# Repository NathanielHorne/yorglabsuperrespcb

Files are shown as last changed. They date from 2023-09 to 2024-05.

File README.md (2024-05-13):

# yorglabsuperrespcb

# Table of Contents
1. [SUMMARY](#SUMMARY)
2. [PCB](#PCB)
3. [CODE](#CODE)
4. [OPERATION](#OPERATION)

## SUMMARY
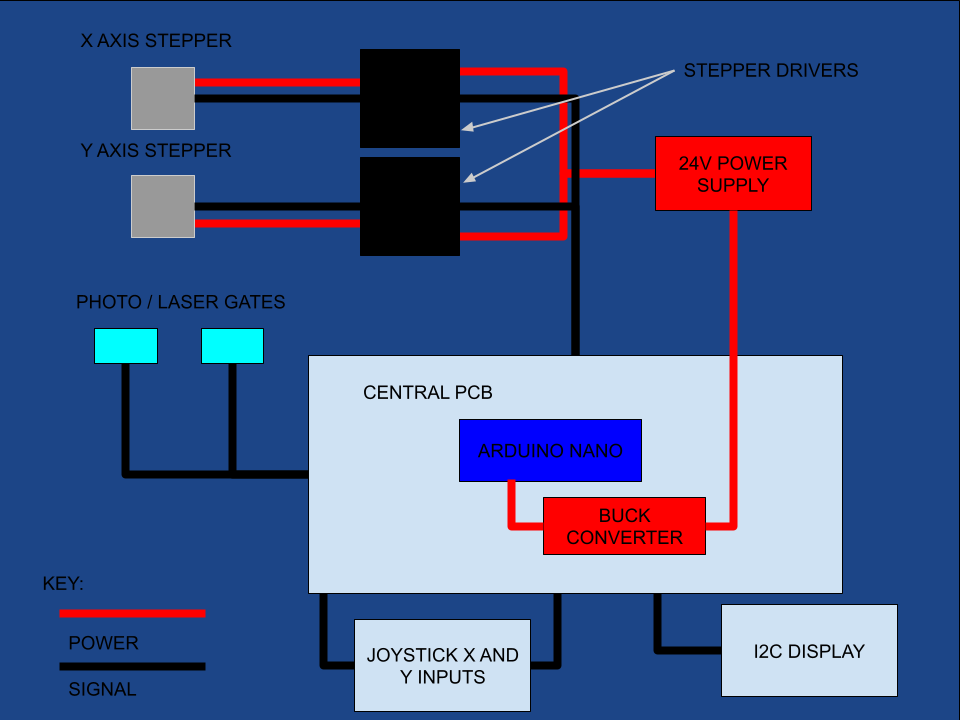
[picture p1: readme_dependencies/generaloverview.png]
Project overview

## PCB
  ### Overview
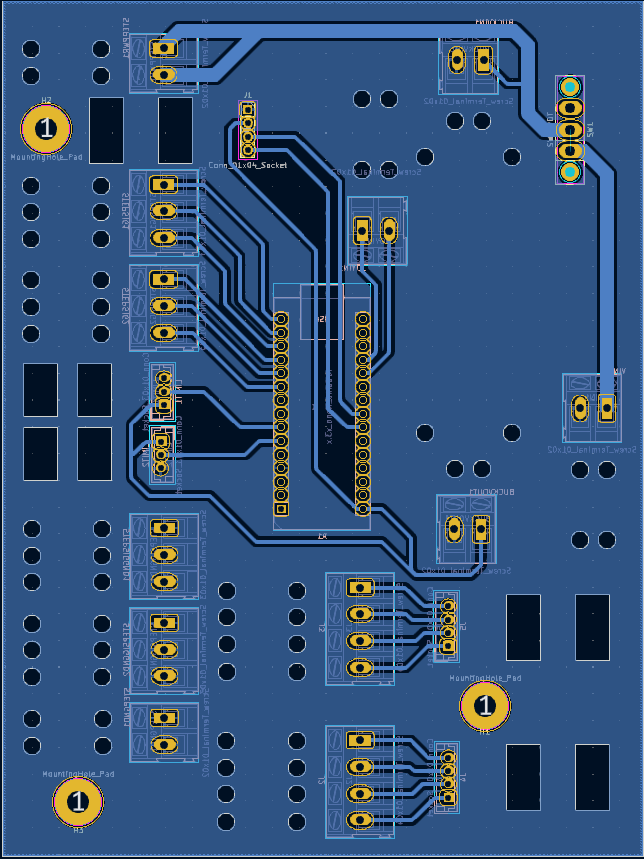
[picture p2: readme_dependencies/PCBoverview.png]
PCB overview
  
  
  The PCB looks nasty, but is more simple than it appears, at first.
  ***
  ### Where Was it Milled?
  Just as some general background, the board was milled and cut out at the BYU Electrical Engineering Experiential Learning Center. At the time of manufacture, they had yet to integrate solder masks. So, any pictures given of the fully-assembled board will show only *bare copper*. Future iterations should have a solder mask for safety reasons.
  ***
  ### Tension Relief Holes
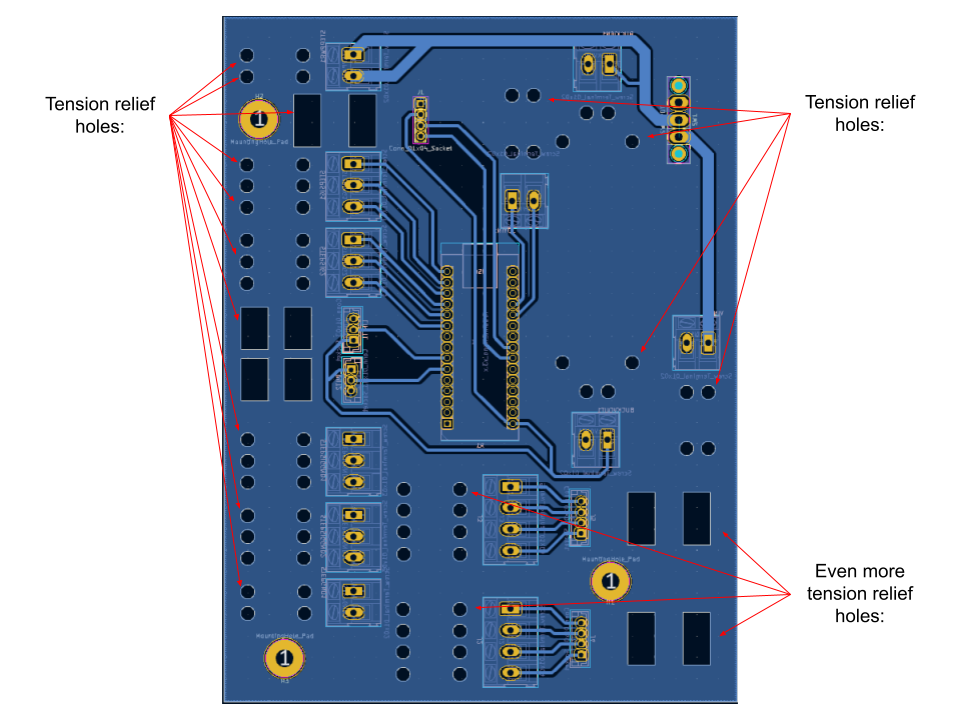
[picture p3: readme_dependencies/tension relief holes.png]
Tension relief holes indication
  
  
  Probably the most striking thing to see, at first, are the tension relief holes. You thread the wires or ribbon cables through them like a needle and thread. This makes it so that the tension of any motion / movement on the wires from the outside is transfered to the board instead of the connectors. This adds durability to the board, but also makes it so that it's more complicated to manufacture. Luckily, the BYU Electrical Engineering Experiential Learning Center was able to mill it with little issue.
  ***
  ### Mounting Holes
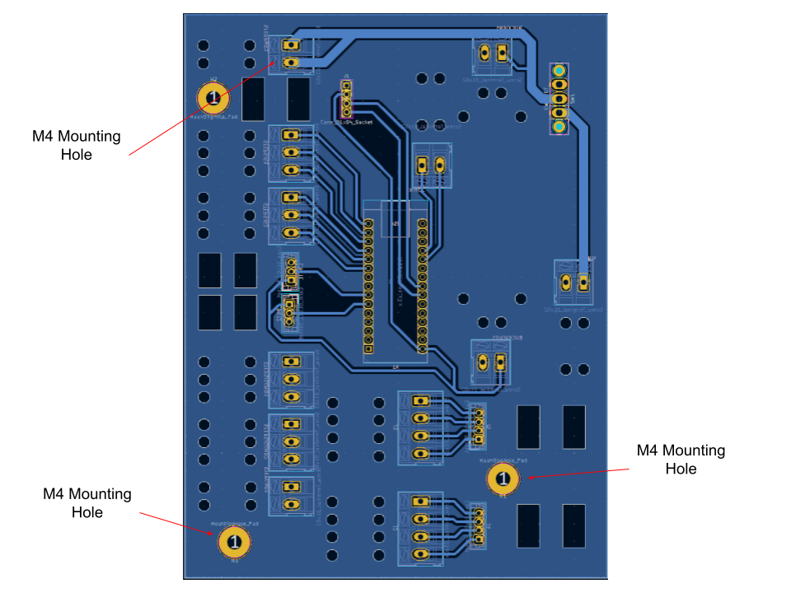
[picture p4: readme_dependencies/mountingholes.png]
Mounting holes identification
  

  These help mount the PCB to a backing plate. These aren't utilized in our current setup.
  ***
  ### Power Network
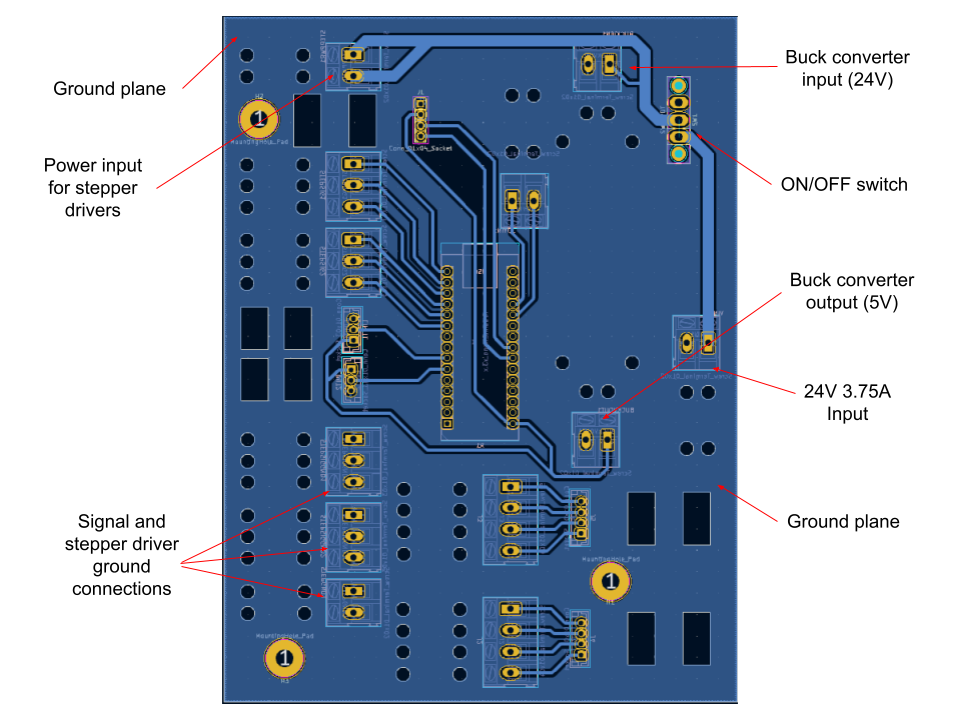
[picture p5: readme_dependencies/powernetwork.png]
Power network identification
  
  ***
  ### Signal Network
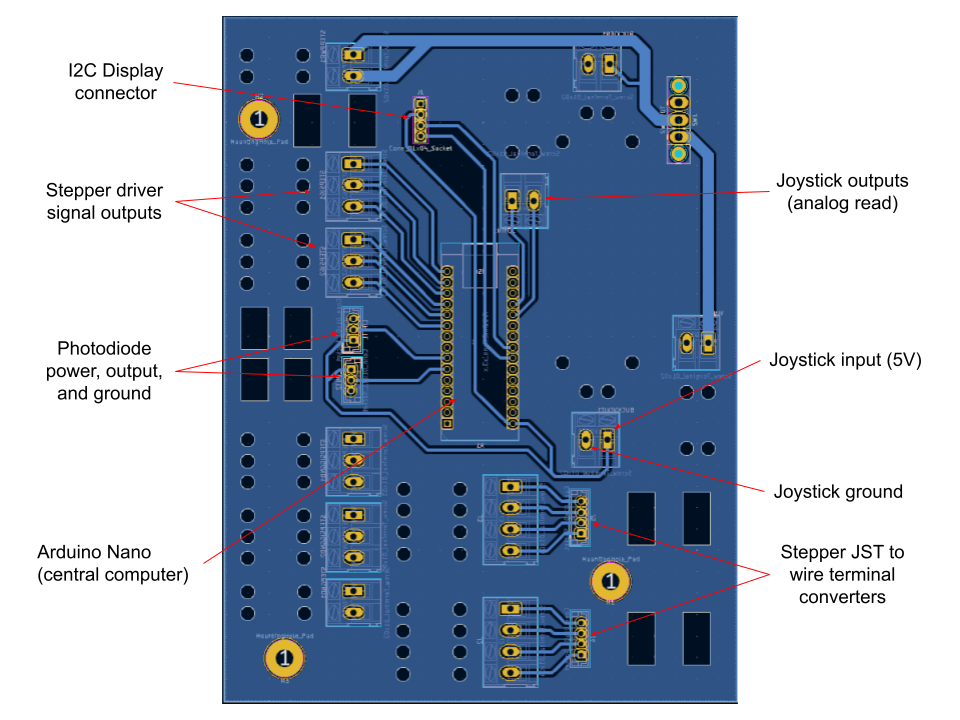
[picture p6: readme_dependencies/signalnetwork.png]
Signal network identification
  
  
  A note about the joystick: the joystick is comprised of two potentiometers (variable resistors). The Nano is able to convert voltage inputs from 0V - 5V and convert it to a value of 0 - 1024 using `analogRead([pin name])`. By running the output of the variable end of the potentiometer to a pin corresponding to the X and Y axis, we're able to measure the angle at which the joystick is currently at. This helps to inform the speed each motor takes on. The more extreme the angle of the joystick on a particular axis, the faster the motor on that particular axis is.
  ***

## CODE
  ### Limitations
  The code isn't perfect. Memory leaks and other performance issues may exist. In addition, the code doesn't neccessarily *need* to be in a single file. Other issues may exist to others. Input in the "issues" page of this repo would be much appreciated. Because an arduino nano cannot support multithreading, minimizing memory leaks and improving speeds are paramount.

  The photogates also aren't used, currently. Therefore, there is no safety preventing the device from moving beyond its intended limits. This is a *major* bug that needs to be fixed immediately.
  ***
  ### Methodology
  In general, any variable used is either inumerated using the `#define` command or is passed by reference. This helps improve the speed at which the code iterates and the amount of memory used. These things can still be improved upon, however.
  ***
  This code is broken up into three distinct sections: perception, planning, and action.
  ```cpp
  perception();
  ```
  This is where the inputs from the various sensors the nano uses are measured and saved. Currently, just the input of the joystick is read, but in the future, this is where one would check whether or not the laser gates are tripped or not, for example.
  ```cpp
  planning();
  ```
  This is where actions are prepped. In our case, this is where the direction and speed of the stepper motors is calculated.
  ```cpp
  action();
  ```
  In this section, the nano executes the actions we had prepared.
  
  *Every other method in the code is an appendage to these three methods*
  
  ***
  ### Startup
  An attempt was made to create a movement sequence that would automatically "home" the stage, setting the stepper's default state to one extreme of their movement. This would allow the laser gates to prevent the stage from moving beyond their limits. This was never acheived. This also makes it so that the I2C display doesn't display location information (another desired goal with startup)
  ### Custom Step Signal
  In order for each stepper to increment, the "step" pin needs to receive a distinct off-on-off pattern. The rate at which these patterns come in dictates the rate at which the stepper increments, changing its speed. 
  The Arduino Nano's hardware natively supports "pulse width modulation" (PWM) that *could* be used to accomplish this. However, PWM signals are generally set at a specific frequency. This would make it so that the steppers would step at a fixed rate regardless of the joystick's orientation. 
  
  Because of these limitations, a way of delivering this signal was created using the Nano's internal clock and digital pins:
  ```cpp
  void move_stepper(const unsigned int& step_pin, unsigned long& time_index, const unsigned int& time_tolerance, const unsigned int& direction_bool, int64_t& num_steps, const int& ena) {
    if ((micros() - time_index) > time_tolerance) {
      digitalWrite(step_pin, HIGH);
      digitalWrite(step_pin, LOW);
      if (ena == LOW) {
        if(direction_bool == HIGH) {
          num_steps++;
        }
        else if (direction_bool == LOW) {
          num_steps--;
        }
      }
      time_index = micros();
    }
  }
  ```
  At its core, this method manually defines how long the arduino takes in-between stepping each motor. This is done by storing when the nano begins to wait using the `micros();` command, then measuring how much time has past. If the elapsed time is larger than the defined wait time, the nano commands the stepper to take a single step, the number of total steps that stepper has taken is recorded, and the process begins again. 
  The wait time is defined at the very top of the file. See the variables `slowest_speed`, `second_fastest`, `second_slowest`, and `fastest_speed` in the `#define` section of the code.
  ***
  ### A Note About Printing the Relative Position of the Stage
  In the event that we wanted to plot the relative position of the stage, we would need to display the number of steps the stepper has taken in relation to when it was homed. Turns out, the number of steps a stepper takes traversing accross one of the metal fins the photodiode uses to tell whether or not the stepper is out of alignment is about the max value of the variable type "long long" or "int64_t". Obviously, this is kind of insane. It also leads to other errors. 
  ***
## OPERATION
Ensure every wire is connected to where it needs to be connected to. Position the stage so the path of the photodiodes is blocked by their corresponding metal fin. Plug the stage's power supply into a wall socket. Turn the motherboard on by flipping the switch. A blue and red indicator light from the buck converter and Arduino Nano respectively should come on immediately. From then on, use the joystick to move the stage. The higher the angle of the joystick in either direction, the faster the steppers will step in that direction.

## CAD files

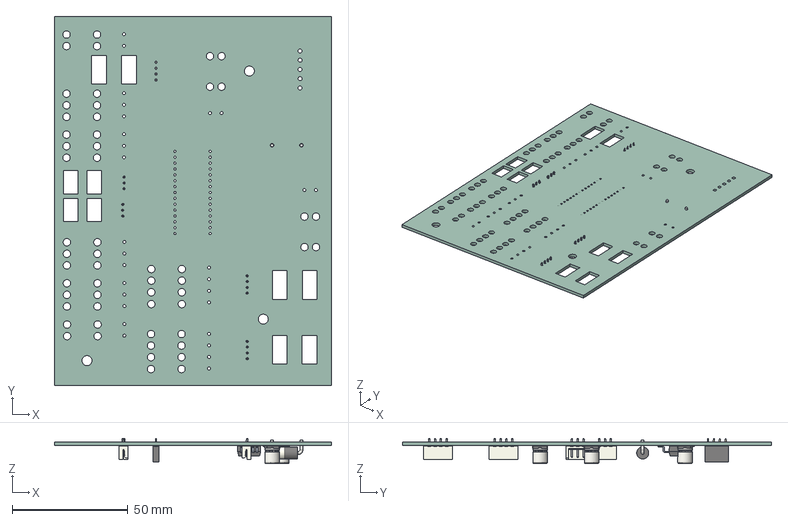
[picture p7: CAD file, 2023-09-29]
stepper_stage_PCB/stepper_microscope_stage/stepper_microscope_stage.step
119.9 x 159.6 x 10.9 mm
stepper_microscope_stage PCB

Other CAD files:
stepper_stage_PCB/assembly_outputs/3Dprintedsolderstencil/stepper_microscope_stage-B_Paste.dxf

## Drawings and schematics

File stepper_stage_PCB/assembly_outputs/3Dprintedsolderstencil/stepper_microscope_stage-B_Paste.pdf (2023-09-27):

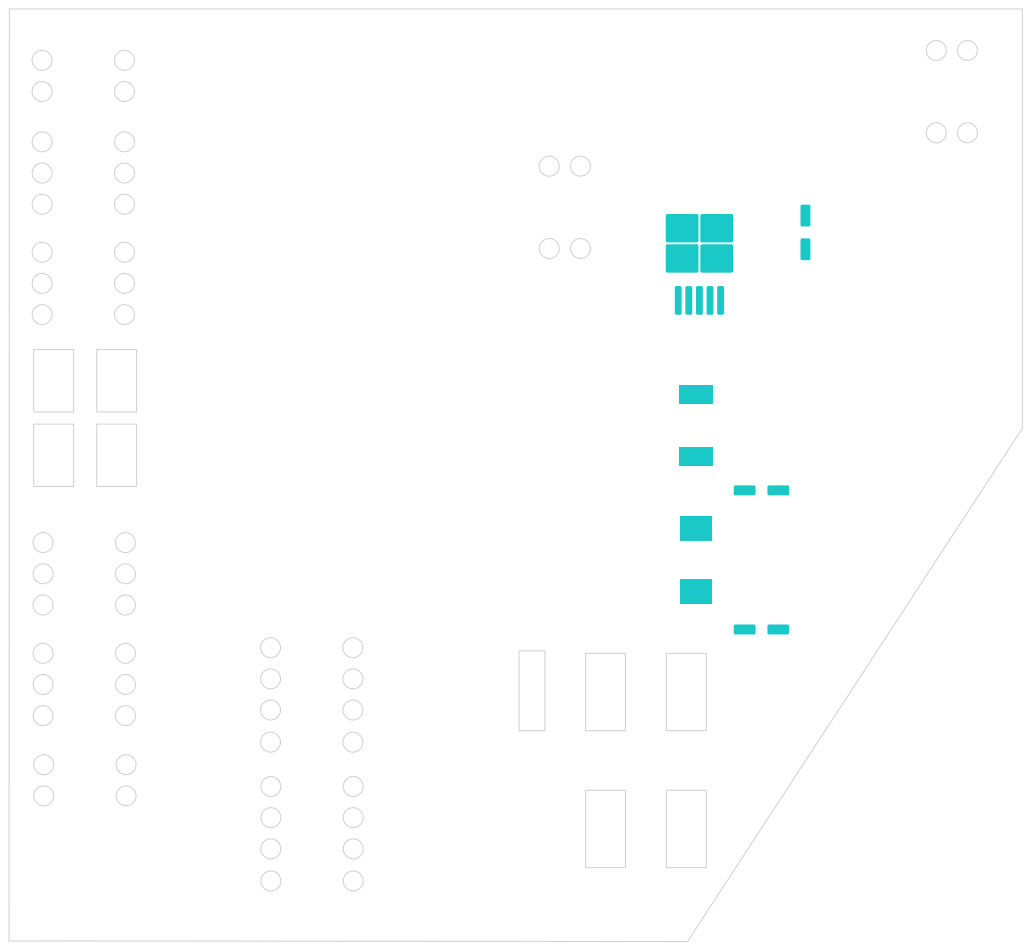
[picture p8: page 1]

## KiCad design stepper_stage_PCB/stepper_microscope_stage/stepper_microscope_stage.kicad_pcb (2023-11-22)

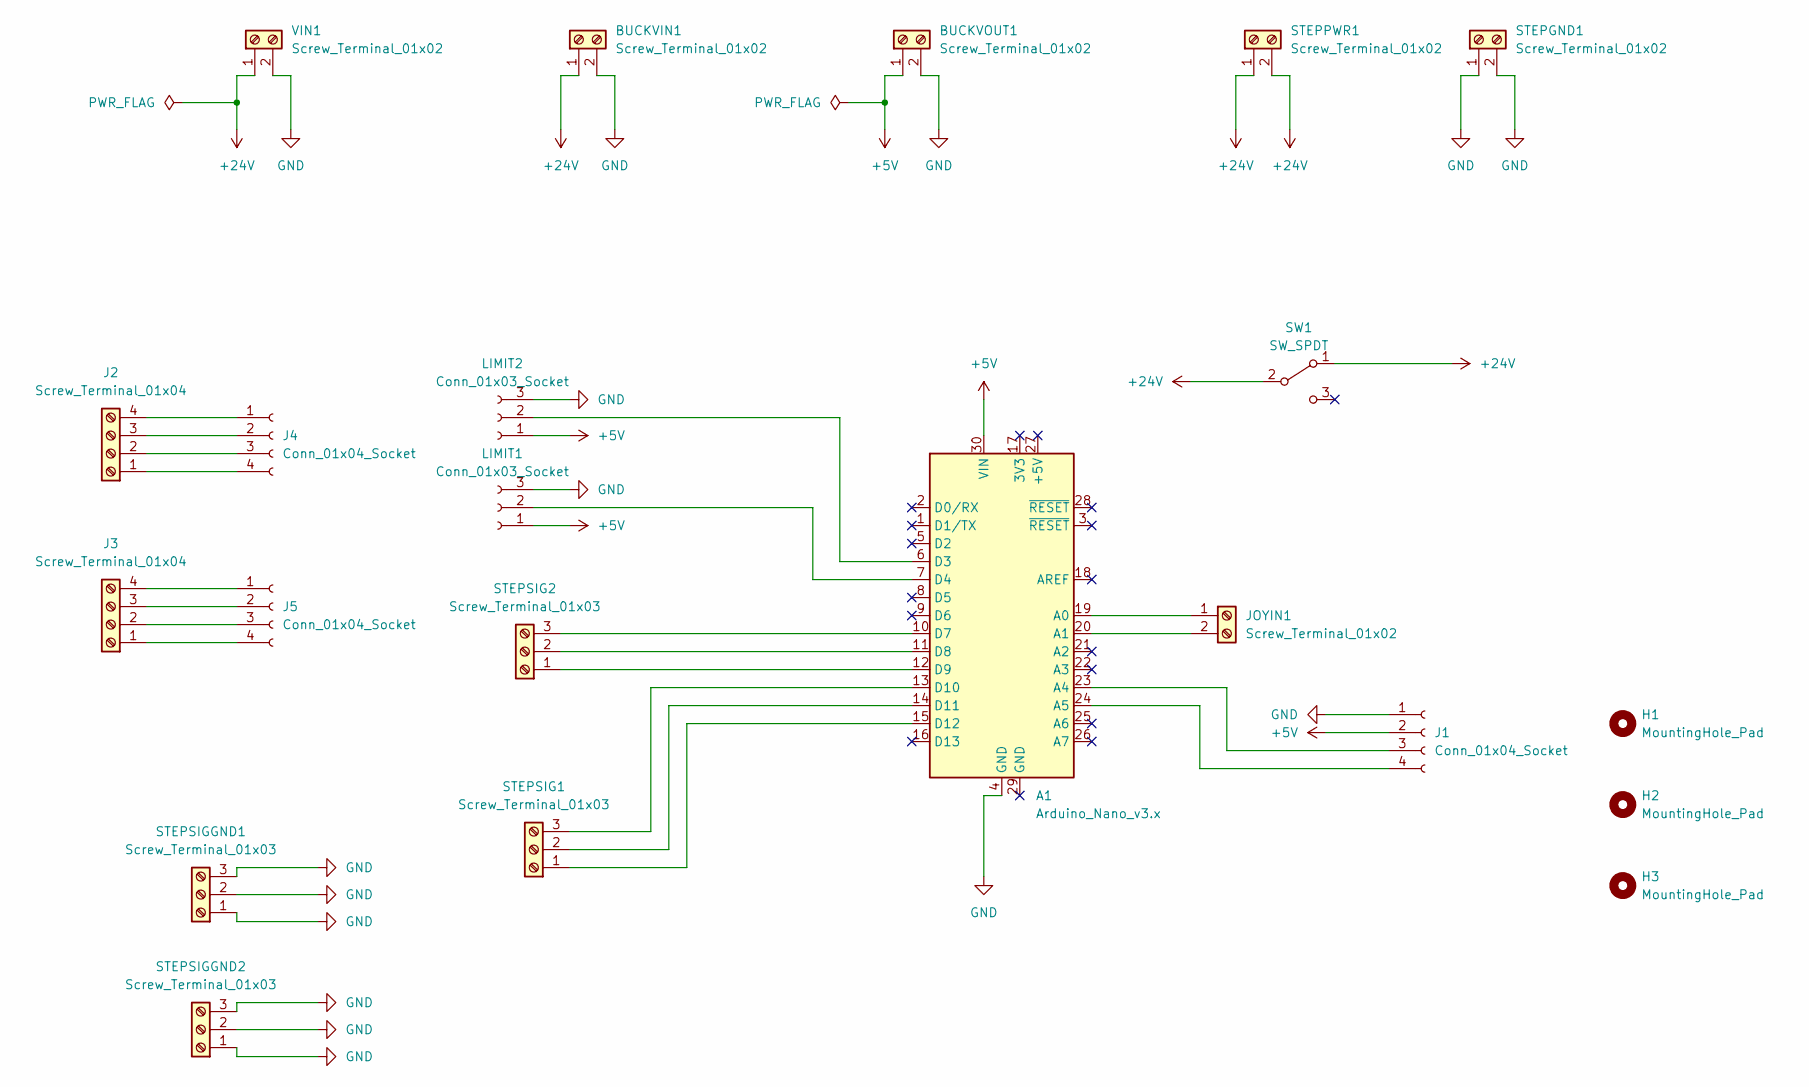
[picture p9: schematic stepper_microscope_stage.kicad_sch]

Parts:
A1: Arduino_Nano_v3.x; Arduino_Nano
BUCKVIN1: Screw_Terminal_01x02; TerminalBlock_Altech_AK300-2_P5.00mm
BUCKVOUT1: Screw_Terminal_01x02; TerminalBlock_Altech_AK300-2_P5.00mm
H1, H2, H3: MountingHole_Pad; MountingHole_4.3mm_M4_Pad
J1: Conn_01x04_Socket; PinSocket_1x04_P2.54mm_Vertical
J2, J3: Screw_Terminal_01x04; TerminalBlock_Altech_AK300-4_P5.00mm
J4, J5: Conn_01x04_Socket; JST_EH_B4B-EH-A_1x04_P2.50mm_Vertical
JOYIN1: Screw_Terminal_01x02; TerminalBlock_Altech_AK300-2_P5.00mm
LIMIT1, LIMIT2: Conn_01x03_Socket; JST_EH_B3B-EH-A_1x03_P2.50mm_Vertical
STEPGND1: Screw_Terminal_01x02; TerminalBlock_Altech_AK300-2_P5.00mm
STEPPWR1: Screw_Terminal_01x02; TerminalBlock_Altech_AK300-2_P5.00mm
STEPSIG1, STEPSIG2: Screw_Terminal_01x03; TerminalBlock_Altech_AK300-3_P5.00mm
STEPSIGGND1, STEPSIGGND2: Screw_Terminal_01x03; TerminalBlock_Altech_AK300-3_P5.00mm
SW1: SW_SPDT; spdt_4mm_pitch_with_tension_relief
VIN1: Screw_Terminal_01x02; TerminalBlock_Altech_AK300-2_P5.00mm

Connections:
+5V: A1.30 (VIN), BUCKVOUT1.1, J1.2, LIMIT1.1, LIMIT2.1
+24V: BUCKVIN1.1, STEPPWR1.1, STEPPWR1.2, SW1.1 (A), SW1.2 (B), VIN1.1
GND: A1.4 (GND), BUCKVIN1.2, BUCKVOUT1.2, J1.1, LIMIT1.3, LIMIT2.3, STEPGND1.1, STEPGND1.2, STEPSIGGND1.1, STEPSIGGND1.2, STEPSIGGND1.3, STEPSIGGND2.1, STEPSIGGND2.2, STEPSIGGND2.3, VIN1.2
unnamed: A1.19 (A0), JOYIN1.1
unnamed: A1.20 (A1), JOYIN1.2
unnamed: A1.23 (A4), J1.3
unnamed: A1.24 (A5), J1.4
unnamed: A1.6 (D3), LIMIT2.2
unnamed: A1.7 (D4), LIMIT1.2
unnamed: A1.10 (D7), STEPSIG2.3
unnamed: A1.11 (D8), STEPSIG2.2
unnamed: A1.12 (D9), STEPSIG2.1
unnamed: A1.13 (D10), STEPSIG1.3
unnamed: A1.14 (D11), STEPSIG1.2
unnamed: A1.15 (D12), STEPSIG1.1
unnamed: J2.1, J4.4
unnamed: J2.2, J4.3
unnamed: J2.3, J4.2
unnamed: J2.4, J4.1
unnamed: J3.1, J5.4
unnamed: J3.2, J5.3
unnamed: J3.3, J5.2
unnamed: J3.4, J5.1

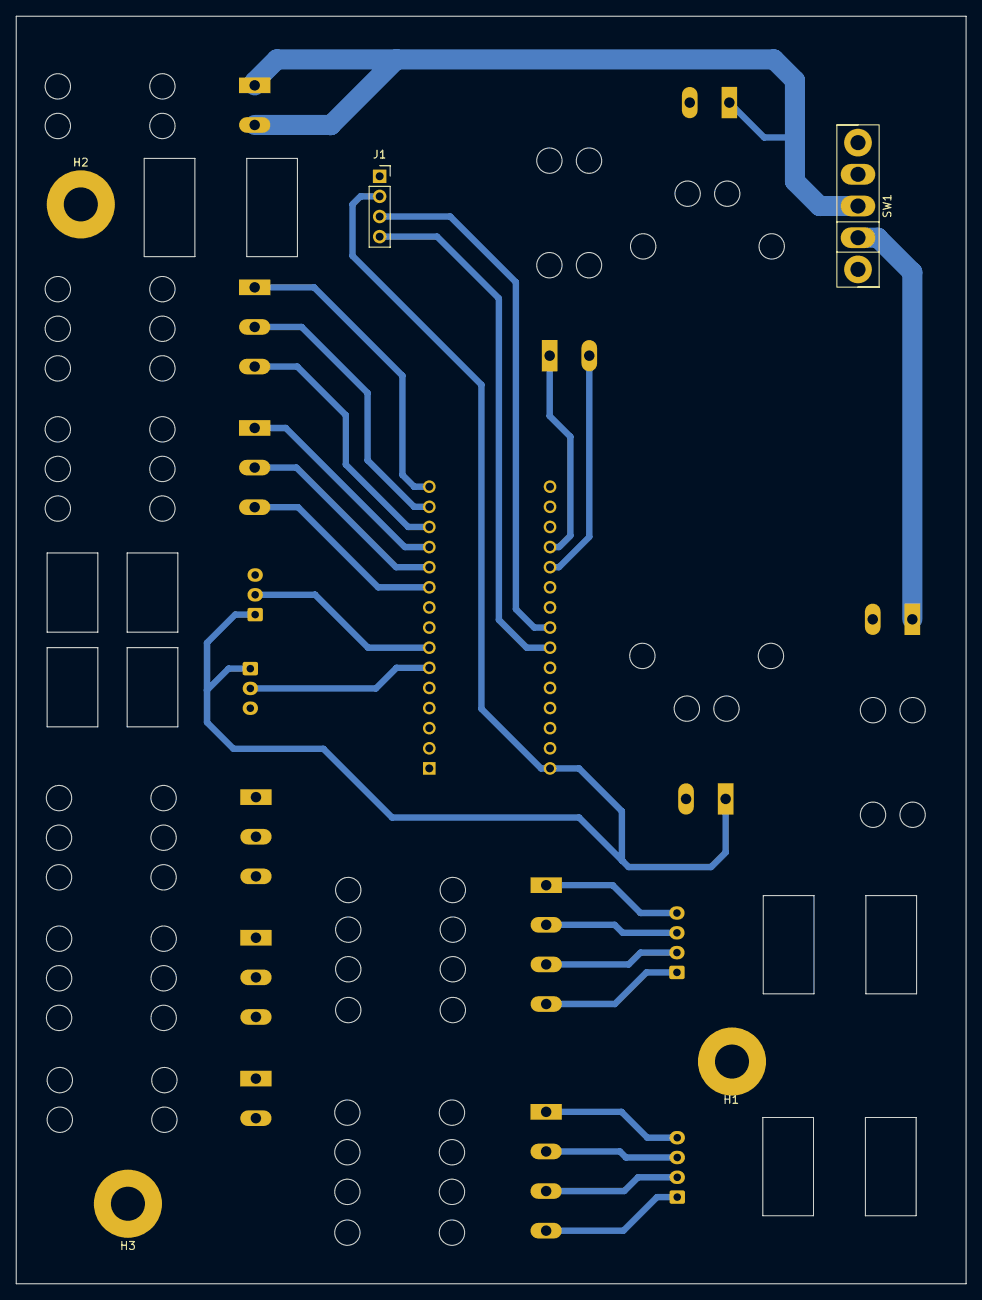
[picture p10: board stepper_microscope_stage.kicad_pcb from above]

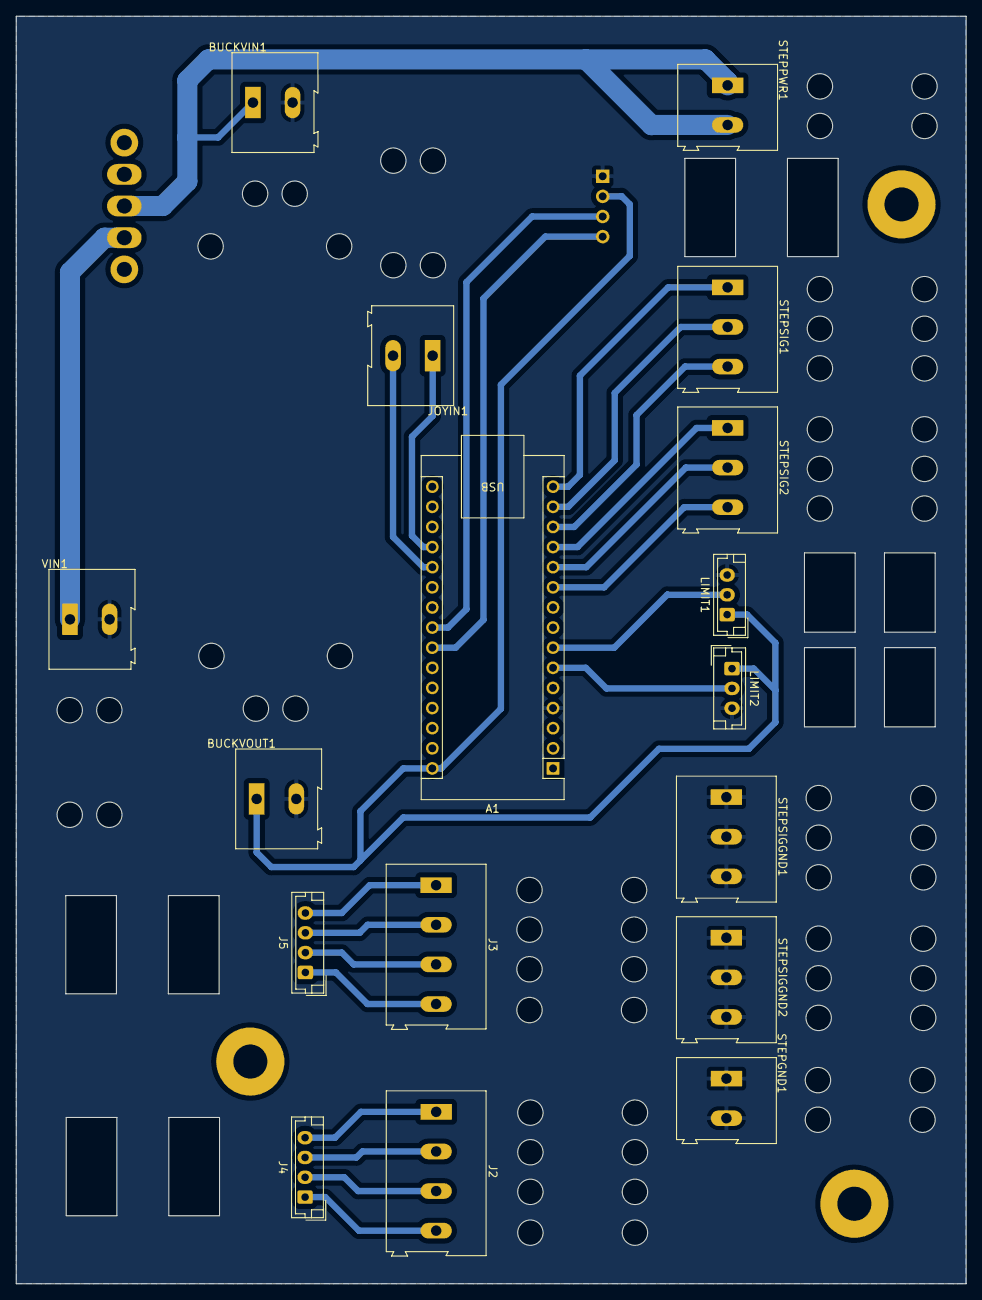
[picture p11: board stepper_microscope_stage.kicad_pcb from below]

Board: 2 copper layers, 119.9 x 160.0 mm, 22 parts (17 on the bottom side), 23 nets.

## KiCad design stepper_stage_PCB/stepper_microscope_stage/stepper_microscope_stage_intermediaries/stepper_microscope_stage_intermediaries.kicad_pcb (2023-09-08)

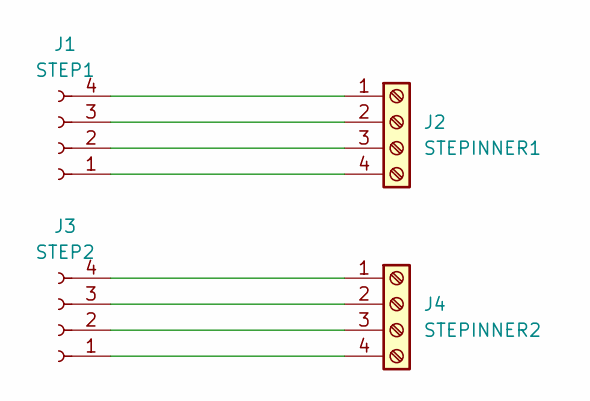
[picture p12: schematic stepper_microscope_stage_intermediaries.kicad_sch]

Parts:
J1: STEP1; Molex_CLIK-Mate_502382-0470_1x04-1MP_P1.25mm_Vertical
J2: STEPINNER1; TerminalBlock_Altech_AK300-4_P5.00mm
J3: STEP2; Molex_CLIK-Mate_502382-0470_1x04-1MP_P1.25mm_Vertical
J4: STEPINNER2; TerminalBlock_Altech_AK300-4_P5.00mm

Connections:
unnamed: J1.1, J2.4
unnamed: J1.2, J2.3
unnamed: J1.3, J2.2
unnamed: J1.4, J2.1
unnamed: J3.1, J4.4
unnamed: J3.2, J4.3
unnamed: J3.3, J4.2
unnamed: J3.4, J4.1

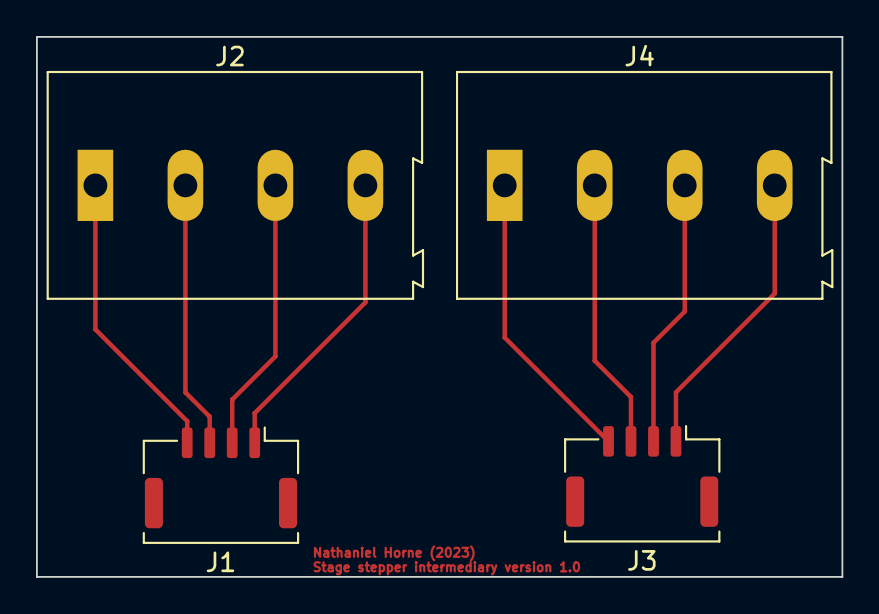
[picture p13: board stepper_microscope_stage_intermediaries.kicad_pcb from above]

Board: 2 copper layers, 44.8 x 30.0 mm, 4 parts (0 on the bottom side), 8 nets.

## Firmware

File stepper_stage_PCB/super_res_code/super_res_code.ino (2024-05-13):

#include <math.h>

// Stepper box 1 I/O pin definitions
#define stepPin1  10
#define dirPin1   11
#define enPin1    12

// Stepper box 2 I/O pin definitions
#define stepPin2  9
#define dirPin2   8
#define enPin2    7

// Dual axis joystick I/O definitions 
#define joy_in1   A1
#define joy_in2   A0

// Optical gate switches I/O definitions
#define gate_switch1 4
#define gate_switch2 3

// Proven deadzone = 200
#define joy_deadzone 200

#define analog_in_max_range   880
#define analog_in_half_range  analog_in_max_range/2

// How long the stepper should wait in microseconds between steps 
#define startup_speed         700
#define slowest_speed         7000
#define second_fastest        3500
#define second_slowest        1453
#define fastest_speed         700

// Any analog read value outside of this zone is automatically disregarded
#define movement_zone         (analog_in_half_range-joy_deadzone)

/* This defines different speed regions based on the joystick's angle
   This is based off of the joystick's angle from in the "middle" position
   The middle position is also 512 according to analogRead();
*/
#define limit_1               280
#define limit_2               360
#define limit_3               400

// Define the global variables for stepper 1 
unsigned int joy_input1 = 0;
int ena1 = LOW;
int direction_bool1 = LOW;
unsigned long step_1_time_index = micros();
unsigned int step_1_time_tolerance = 0;
int64_t num_steps1 = 0;
// These variables were supposed to be used during the initial startup sequence
// This seequence hasn't been perfected yet. 
int is_off_track1 = LOW;
int is_at_middle1 = LOW;

int midpoint = 0; 

// Define the global variables for stepper 2
unsigned int joy_input2 = 0;
int ena2 = LOW;
int direction_bool2 = HIGH;
unsigned long step_2_time_index = micros();
unsigned int step_2_time_tolerance = 0;
int64_t num_steps2 = 0;
int is_off_track2 = LOW;
int is_at_middle2 = LOW;

void get_joystick_inputs();

void get_is_off_tracks();

void get_back_on_track();

void set_direction_bools();

void set_en_pins();

void startup();

void perception();

void joystick_direction(const int& in, int& dir, int& ena, const int& off_track);

unsigned int stepper_wait_time(const int& input);

void planning();

void move_stepper(const unsigned int& step_pin, unsigned long& time_index, const unsigned int& time_tolerance, const unsigned int& direction_bool, int64_t& num_steps, const int& ena);

void action();

void print(uint64_t value);

unsigned int uint64_to_int(uint64_t value) {
  int return_value = 0;
  for (int i = 0; i < 2000; i++) {
    value /= 10;
  }
  return_value = value;
  return return_value;
}

void setup() {
  Serial.begin(9600);
  
  // Setup pins for stepper driver 1
  pinMode(stepPin1, OUTPUT);
  pinMode(dirPin1, OUTPUT);
  pinMode(enPin1, OUTPUT);
  
  // Setup pins for stepper driver 1
  pinMode(stepPin2, OUTPUT);
  pinMode(dirPin2, OUTPUT);
  pinMode(enPin2, OUTPUT);

  // Setup joystick inputs
  pinMode(joy_in1, INPUT);
  pinMode(joy_in2, INPUT);

  // Setup photodiode inputs
  pinMode(gate_switch1, INPUT);
  pinMode(gate_switch2, INPUT);
  
  // Enable stepper driver
  set_en_pins();

  // Set stepper driver directions
  set_direction_bools();

//  startup();
}

void loop() {
  // This is the core of the code. The Nano repeats this code indefinitely

  perception();

  planning();

  action();
}

void get_joystick_inputs() {
  joy_input1 = analogRead(joy_in1);
  joy_input2 = analogRead(joy_in2);
}

void get_is_off_tracks() {
  // Determines whether or not the photodiodes on each axis are triggered or not

  is_off_track1 = digitalRead(gate_switch1);
  is_off_track2 = digitalRead(gate_switch2);
}

void get_back_on_track() {
  /*
  This was an attempt to automate the process of getting the stage to recenter on
  the metal fins on a particular axis. However, this largely failed.
  */

  if(num_steps1 < 0 ){
    direction_bool1 = !direction_bool1;
  }

  if(is_off_track2) {
    direction_bool2 = !direction_bool2;
  }

  set_direction_bools();

  do {
    get_is_off_tracks();
    
    if(is_off_track1) {
      move_stepper(stepPin1, step_1_time_index, startup_speed*4, direction_bool1, num_steps1, ena1);
    }
    
    if(is_off_track2) {
      move_stepper(stepPin2, step_2_time_index, startup_speed*4, direction_bool2, num_steps2, ena2);
    }
  } while(is_off_track1 || is_off_track2);
}

void set_en_pins() {
  digitalWrite(enPin1, ena1);
  digitalWrite(enPin2, ena2);
}

void set_direction_bools() {
  digitalWrite(dirPin1, direction_bool1);
  digitalWrite(dirPin2, direction_bool2);
}

void startup() {
  do {
    get_is_off_tracks();
    
    if(!(is_off_track1)) {
      move_stepper(stepPin1, step_1_time_index, startup_speed, direction_bool1, num_steps1, ena1);
    }
    
    if(!(is_off_track2)) {
      move_stepper(stepPin2, step_2_time_index, startup_speed, direction_bool2, num_steps2, ena2);
    }
  } while(!(is_off_track1) || !(is_off_track2));

  get_back_on_track();

  num_steps1 = 0;
  num_steps2 = 0;
}

void perception() {

  get_joystick_inputs(); 

  get_is_off_tracks();
}

void joystick_direction(const int& in, int& dir, int& ena, const int& off_track) {
  if (in < (analog_in_half_range - joy_deadzone)) {
    // Movement enabled, moving in one direction
    ena = LOW;
    dir = LOW;
  }
  else if (in > (analog_in_half_range + joy_deadzone)) {
    // Movement enabled, moving in opposite direction
    ena = LOW;
    dir = HIGH;
  }
  else {
    // Movement disabled
    ena = HIGH;
  }
}

unsigned int stepper_wait_time(const int& input) {
  // The joystick angle determines the speed of the steppers.
  // This method assigns this speed.

  int scrubbed_input = abs(input - analog_in_half_range);
  if (scrubbed_input >= 0 && scrubbed_input < limit_1) {
    return slowest_speed;
  }
  else if (scrubbed_input >= limit_1 && scrubbed_input < limit_2) {
    return second_slowest; 
  }
  else if (scrubbed_input >= limit_2 && scrubbed_input < limit_3){
    return second_fastest;
  }
  else {
    return fastest_speed;
  }
}

void planning() {
  joystick_direction(joy_input1, direction_bool1, ena1, is_off_track1);
  step_1_time_tolerance = stepper_wait_time(joy_input1);
  
  joystick_direction(joy_input2, direction_bool2, ena2, is_off_track2);
  step_2_time_tolerance = stepper_wait_time(joy_input2);
}

void move_stepper(const unsigned int& step_pin, unsigned long& time_index, const unsigned int& time_tolerance, const unsigned int& direction_bool, int64_t& num_steps, const int& ena) {
  if ((micros() - time_index) > time_tolerance) {
    digitalWrite(step_pin, HIGH);
    digitalWrite(step_pin, LOW);
    if (ena == LOW) {
      if(direction_bool == HIGH) {
        num_steps++;
      }
      else if (direction_bool == LOW) {
        num_steps--;
      }
    }
    time_index = micros();
  }
}

void action() {
  set_en_pins();

  set_direction_bools();

  move_stepper(stepPin1, step_1_time_index, step_1_time_tolerance, direction_bool1, num_steps1, ena1);
  move_stepper(stepPin2, step_2_time_index, step_2_time_tolerance, direction_bool2, num_steps2, ena2); 

//  get_back_on_track();
}

void print(int64_t value){


    const int NUM_DIGITS    = log10(value) + 1;

    char sz[NUM_DIGITS + 1];
    
    sz[NUM_DIGITS] =  0;
    for ( size_t i = NUM_DIGITS; i--; value /= 10)
    {
        sz[i] = '0' + (value % 10);
    }
    
    Serial.println(sz);
}

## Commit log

2023-09-08 Moved existing work to GitHub.
    [stepper_microscope_stage-B_Cu.gbr, stepper_microscope_stage-B_Mask.gbr, stepper_microscope_stage-B_Paste.gbr, stepper_microscope_stage-B_Silkscreen.gbr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]
2023-09-08 Updated mounting holes to be M4 instead of M2
    [stepper_microscope_stage.kicad_pcb, stepper_microscope_stage.kicad_sch]
2023-09-08 Route GND of +24v net.
    [stepper_microscope_stage.kicad_pcb]
2023-09-08 Final 90%
    [stepper_microscope_stage.kicad_pcb]
2023-09-08 Routed and filled board. Missing switch
    [stepper_microscope_stage.kicad_pcb, stepper_microscope_stage.kicad_sch]
2023-09-09 Version 1 acheived!
    [stepper_microscope_stage.kicad_pcb, stepper_microscope_stage.kicad_sch]
2023-09-27 Working. Must add following: (1) LCD space (2) ground plane
    [stepper_microscope_stage-B_Cu.gbr, stepper_microscope_stage-B_Mask.gbr, stepper_microscope_stage-B_Paste.dxf, stepper_microscope_stage-B_Paste.gbr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]
2023-09-28 Large, but works
    [stepper_microscope_stage.kicad_pcb, stepper_microscope_stage.step]
2023-09-29 Experimented with smaller PCB. Reorganized directories to be more clean
    [stepper_microscope_stage-B_Cu.gbr, stepper_microscope_stage-B_Mask.gbr, stepper_microscope_stage-B_Paste.dxf, stepper_microscope_stage-B_Paste.gbr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]
2023-09-29 Forgot to save work. Autosaved backup.
    [stepper_microscope_stage.kicad_pcb]
2023-11-22 Version 0
    Updated PCB, milled that PCB, soldered parts to that PCB, updated code, works as expected except for the following functionalities listed below:
    - Laser gates are non-operational as of yet. This leads to the following:
    - No homing functionality yet
    - No safety measures to ensure the steppers avoid grinding on their bearings
    - True logarithmic speed control
    - Suitable housing
    [stepper_microscope_stage-B_Cu.gbr, stepper_microscope_stage-B_Fab.gbr, stepper_microscope_stage-B_Mask.gbr, stepper_microscope_stage-B_Paste.gbr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]
2024-04-26 Added tension relief indications and where the board was milled.
